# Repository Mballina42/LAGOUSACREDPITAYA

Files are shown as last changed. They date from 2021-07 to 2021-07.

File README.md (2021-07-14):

# HARDWARE PARA LAGO USAC CON RED PITAYA
Este proyecto recopila los avances realizados por [Escaramujo Project and LAGO Project matching hardware ](https://github.com/ECFM-USAC/EscaramujoLagoMatch), realizando cambios en el diseño de la PCB.

  

## Descripción
El diseño busca controlar el voltaje de alimentación para la placa de la base de un PMT Photonix, obteniendo la linea de alimentación principal de la Red Pitaya, a su vez enviar información de temperatura, presión barométrica y GPS. 

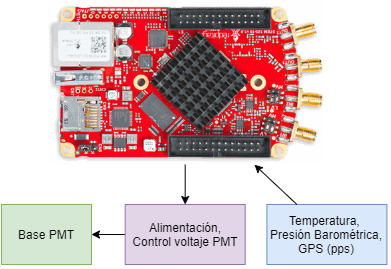
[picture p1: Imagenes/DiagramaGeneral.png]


Dado a que el tipo de voltaje necesitado por la base del PMT debe de ser lineal, la placa debe de proveer los siguientes voltajes:
* 5 VDC (MAX604)
* 3.3 VDC (MAX603)
* 12 VDC 
* 0 - 5 VDC variable
Esta placa se conecta a la base del PMT por medio de un conector RJ45.

Con base en el pinout de la Red Pitaya se utiliza los *pines IDE extension connector*

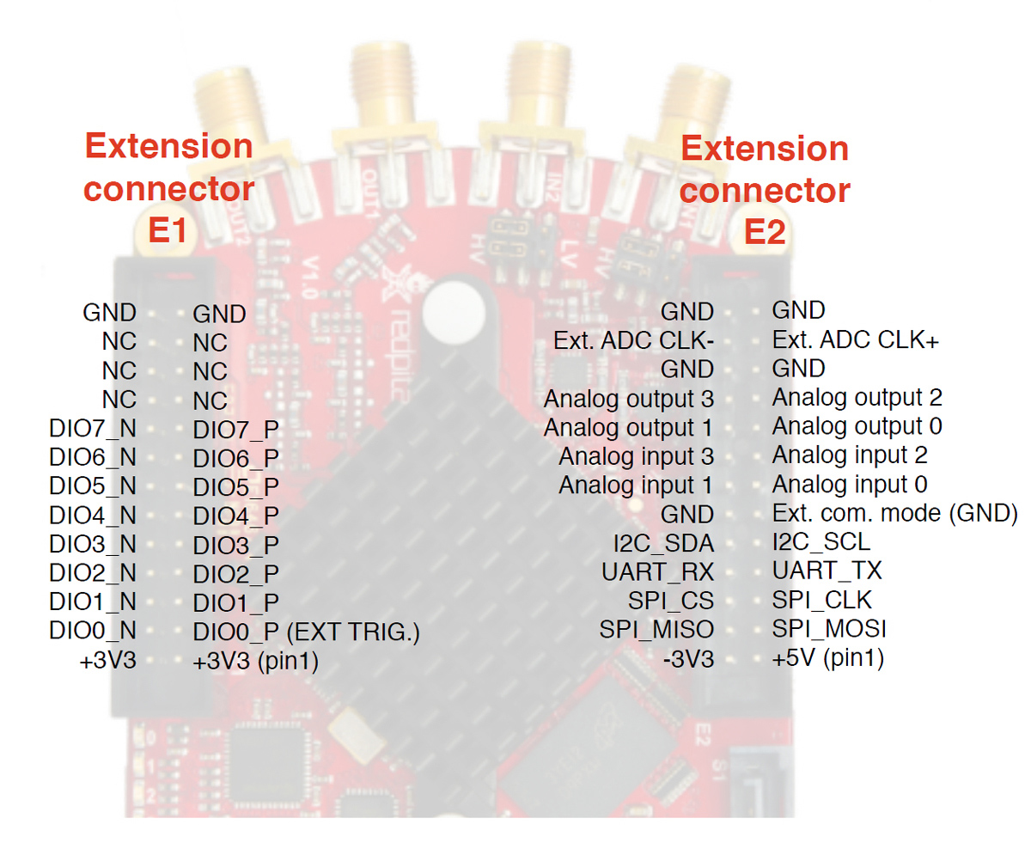
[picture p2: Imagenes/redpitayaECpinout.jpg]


La alimentación de la placa se obtiene del pin +5V.

Se utiliza el modulo BMP180 para la medición de presión barométrica y temperatura, conectado a la Red Pitaya por medio un conector RJ11 utilizando el protocolo de comunicación I2C, con los pines: I2C_SDA y I2C_SCL.

Se utiliza el modulo NEO-6M GPS, conectado por medio de HEADERS IDC y hacia la Red Pitaya por medio de UART_RX, UART_TX y DIO1_N.

Para el control del voltaje se utilizan los pines SPI_CS, SPI_CLK y SPI_MOSI.

[Este es el esquemático del proyecto en formato pdf](Imagenes/esquematico.pdf), también pueden consultarse los editables en la carpeta HARDWARE.

## Resultado final
El diseño del circuito y la PCB se realizaron en el software KiCad. Se muestra el modelo final de la PBC.

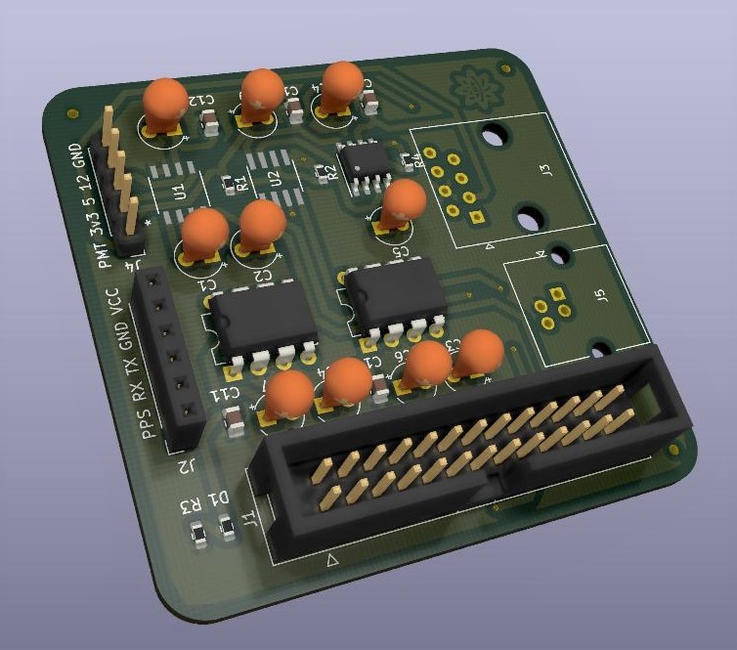
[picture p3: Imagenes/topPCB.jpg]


Dentro de la carpeta Gerber, se encuentra el gerber de cada parte del PCB y dentro de la carpeta CNC_code se encuentra el código para CNC elaborado en el software **FlatCAM**.

## License



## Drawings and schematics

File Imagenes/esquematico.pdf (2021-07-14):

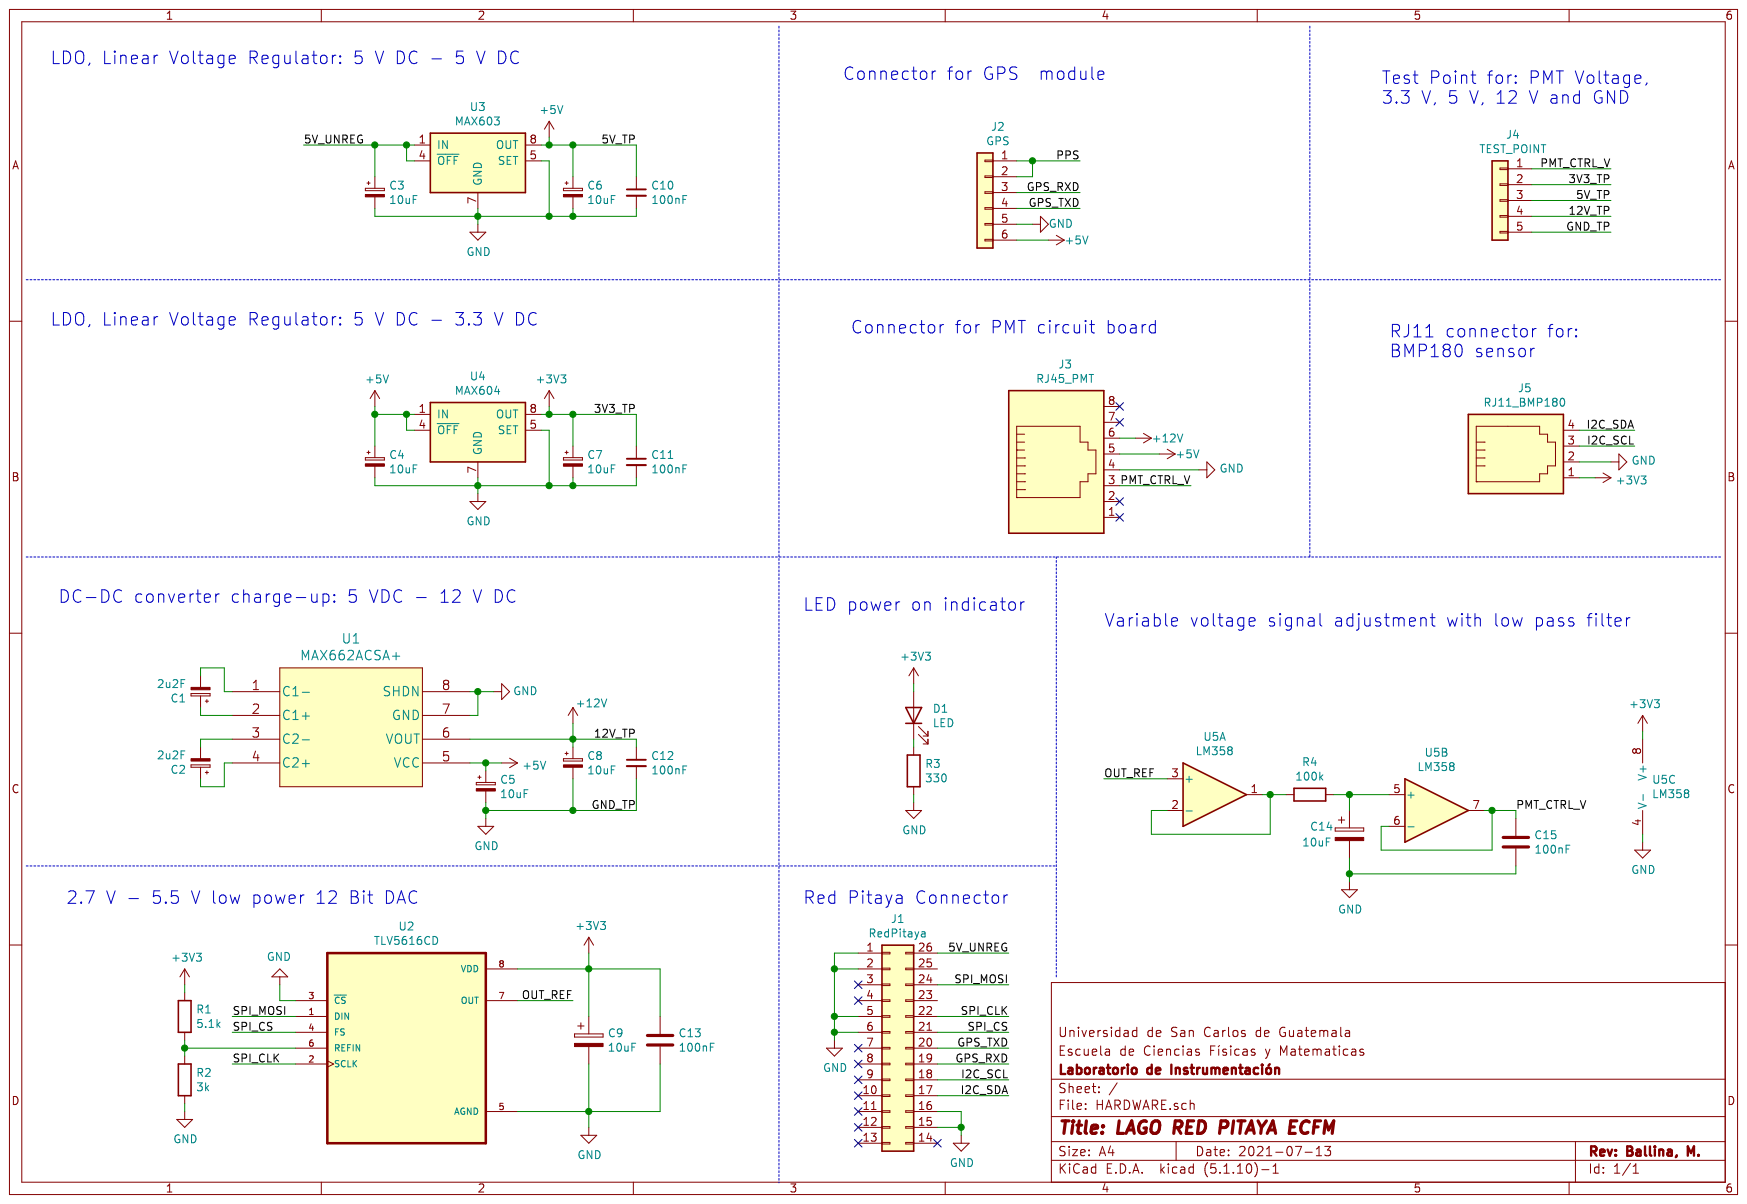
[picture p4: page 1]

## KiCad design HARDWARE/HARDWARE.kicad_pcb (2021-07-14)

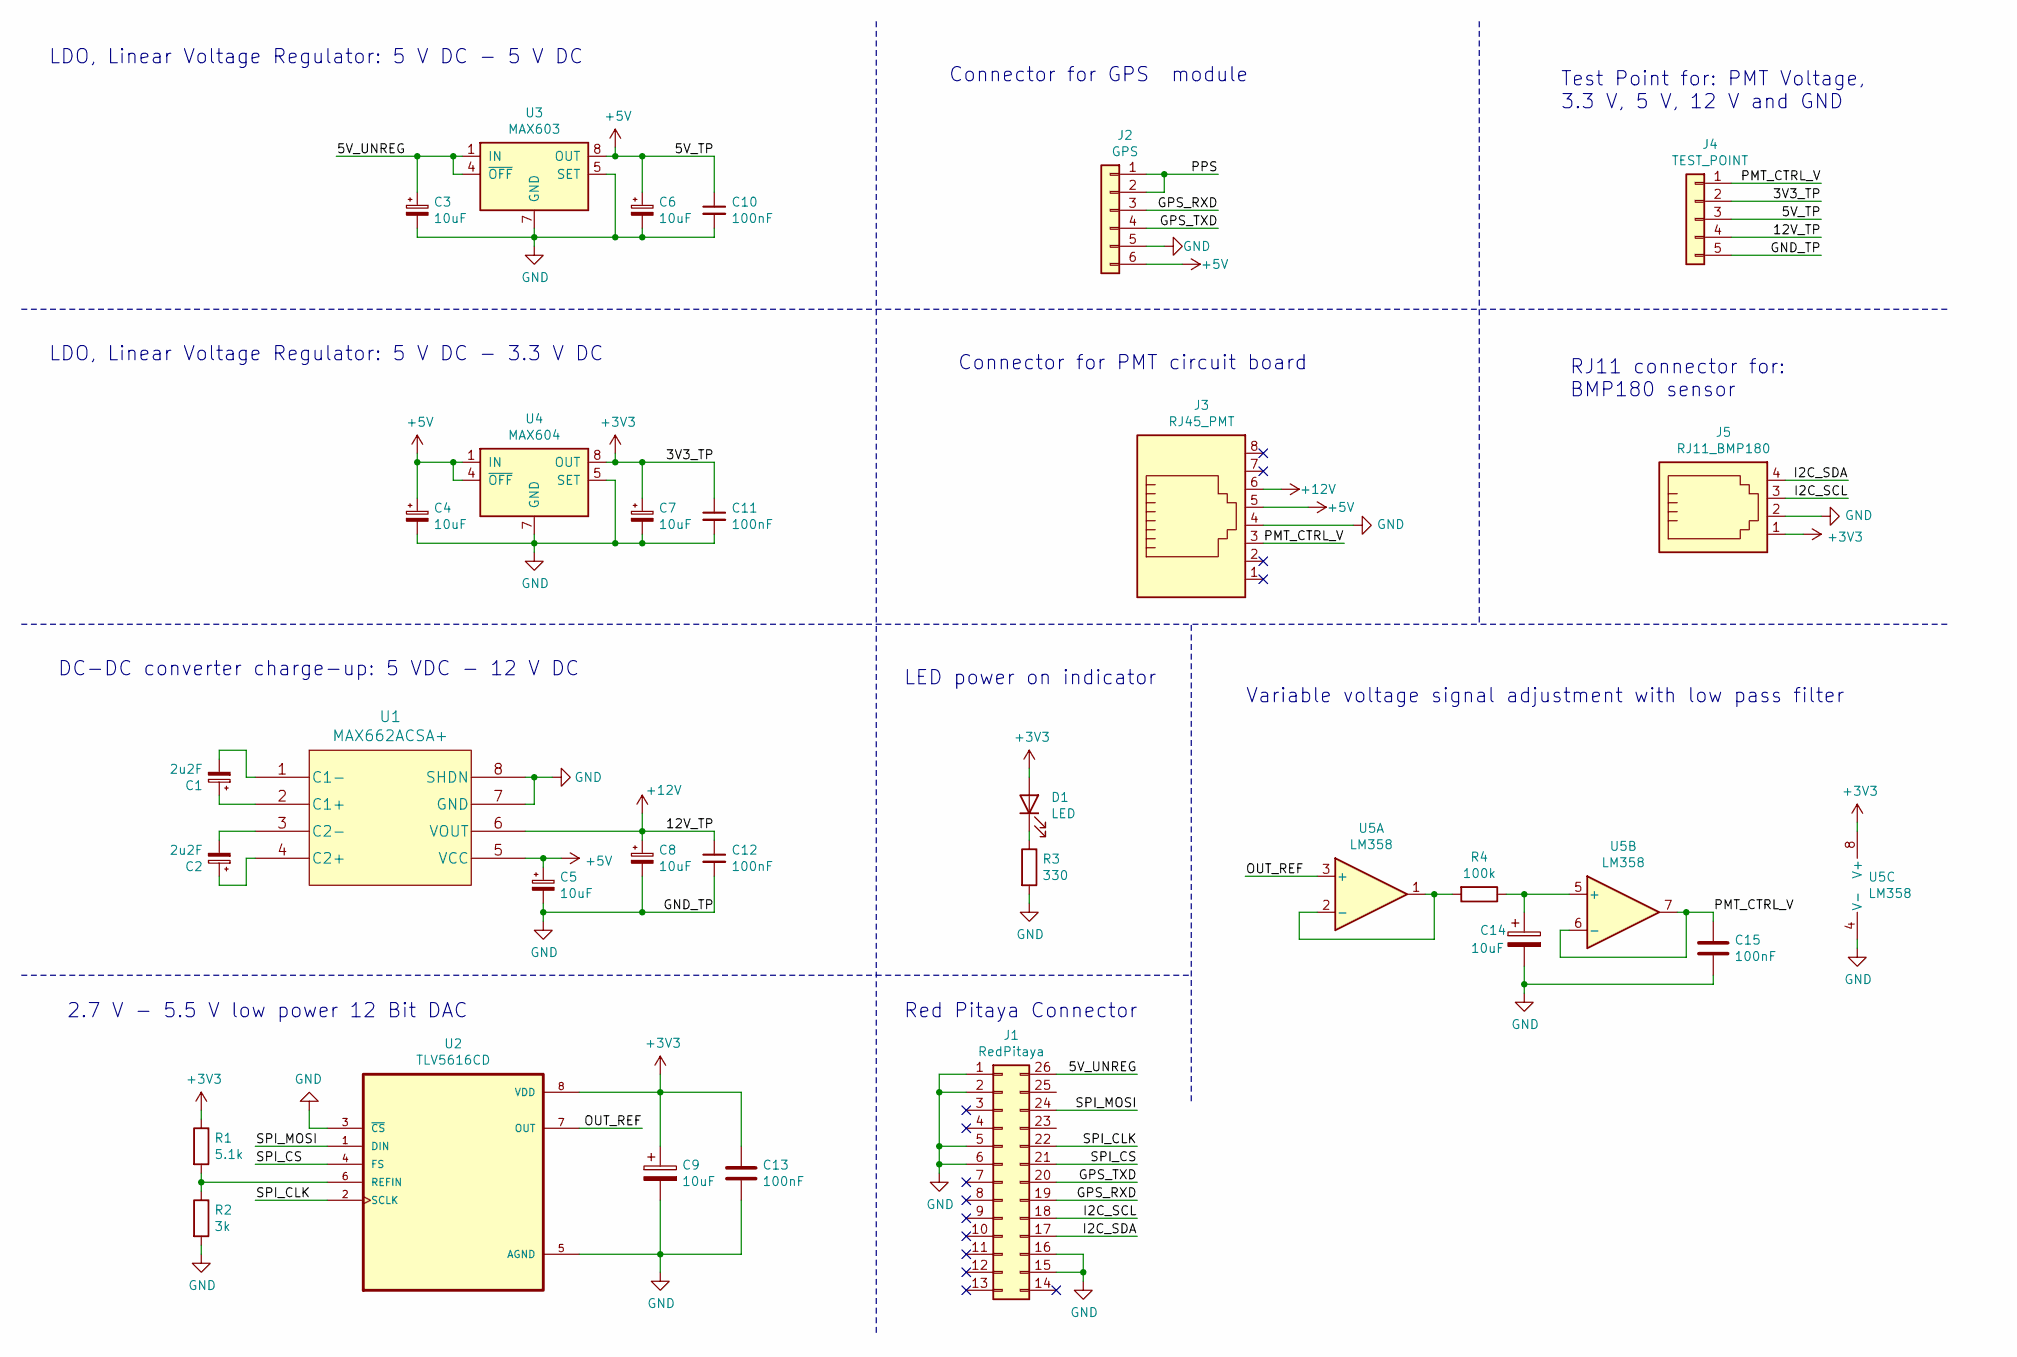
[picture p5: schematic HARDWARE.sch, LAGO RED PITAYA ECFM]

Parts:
C1, C2: 2u2F; CP_Radial_Tantal_D4.5mm_P2.50mm
C3, C4, C5, C6, C7, C8, C9, C14: 10uF; CP_Radial_Tantal_D4.5mm_P2.50mm
C10, C11, C12, C13, C15: 100nF; C_0805_2012Metric
D1: LED; R_0603_1608Metric
J1: RedPitaya; IDC-Header_2x13_P2.54mm_Vertical
J2: GPS; PinSocket_1x06_P2.54mm_Vertical
J3: RJ45_PMT; RJ45_Amphenol_54602-x08_Horizontal
J4: TEST_POINT; PinHeader_1x05_P2.54mm_Vertical
J5: RJ11_BMP180; RJ14_Connfly_DS1133-S4_Horizontal
R1: 5.1k; R_0603_1608Metric
R2: 3k; R_0603_1608Metric
R3: 330; R_0603_1608Metric
R4: 100k; R_0603_1608Metric
U1: MAX662ACSA+; MAX662ACSA&plus_
U2: TLV5616CD; SOIC127P599X175-8N
U3: MAX603; DIP-8_W7.62mm
U4: MAX604; DIP-8_W7.62mm
U5: LM358; SOIC-8_3.9x4.9mm_P1.27mm

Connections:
+3V3: C7.1, C9.1, C11.1, C13.1, D1.2 (A), J4.2, J5.1, R1.1, U2.8 (VDD), U4.8 (OUT), U5.8 (V+)
+5V: C4.1, C5.1, C6.1, C10.1, J2.6, J3.5, J4.3, U1.5 (VCC), U3.8 (OUT), U4.1 (IN), U4.4 (~OFF)
+12V: C8.1, C12.1, J3.6, J4.4, U1.6 (VOUT)
/5V_UNREG: C3.1, J1.26, U3.1 (IN), U3.4 (~OFF)
/GPS_RXD: J1.19, J2.3
/GPS_TXD: J1.20, J2.4
/I2C_SCL: J1.18, J5.3
/I2C_SDA: J1.17, J5.4
/OUT_REF: U2.7 (OUT), U5.3 (+)
/PMT_CTRL_V: C15.1, J3.3, J4.1, U5.6 (-), U5.7
/PPS: J2.1, J2.2
/SPI_CLK: J1.22, U2.2 (SCLK)
/SPI_CS: J1.21, U2.4 (FS)
/SPI_MOSI: J1.24, U2.1 (DIN)
GND: C3.2, C4.2, C5.2, C6.2, C7.2, C8.2, C9.2, C10.2, C11.2, C12.2, C13.2, C14.2, C15.2, J1.1, J1.2, J1.5, J1.6, J1.15, J1.16, J2.5, J3.4, J4.5, J5.2, R2.2, R3.2, U1.7 (GND), U1.8 (SHDN), U2.3 (~CS), U2.5 (AGND), U3.2 (GND), U3.3 (GND), U3.5 (SET), U3.6 (GND), U3.7 (GND), U4.2 (GND), U4.3 (GND), U4.5 (SET), U4.6 (GND), U4.7 (GND), U5.4 (V-)
unnamed: C1.1, U1.2 (C1+)
unnamed: C1.2, U1.1 (C1-)
unnamed: C2.1, U1.4 (C2+)
unnamed: C2.2, U1.3 (C2-)
unnamed: C14.1, R4.1, U5.5 (+)
unnamed: D1.1 (K), R3.1
unnamed: R1.2, R2.1, U2.6 (REFIN)
unnamed: R4.2, U5.1, U5.2 (-)

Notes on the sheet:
LDO, Linear Voltage Regulator: 5 V DC - 5 V DC
LDO, Linear Voltage Regulator: 5 V DC - 3.3 V DC
DC-DC converter charge-up: 5 VDC - 12 V DC
2.7 V - 5.5 V low power 12 Bit DAC
Connector for GPS module
Test Point for: PMT Voltage, 3.3 V, 5 V, 12 V and GND
Variable voltage signal adjustment with low pass filter
LED power on indicator
Red Pitaya Connector
Connector for PMT circuit board
RJ11 connector for: BMP180 sensor

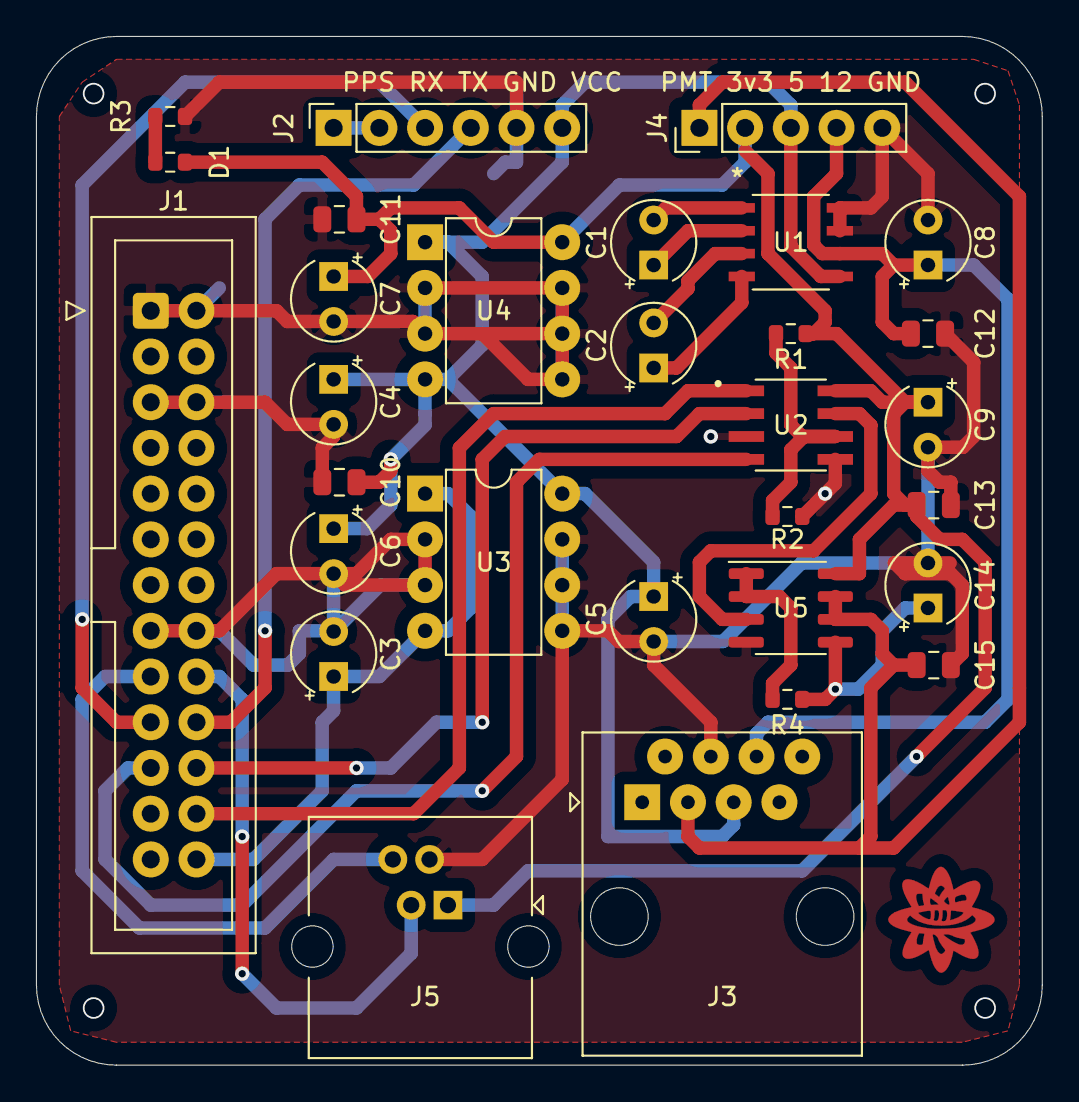
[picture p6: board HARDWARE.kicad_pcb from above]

Board: 2 copper layers, 55.9 x 57.1 mm, 30 parts (0 on the bottom side), 23 nets.

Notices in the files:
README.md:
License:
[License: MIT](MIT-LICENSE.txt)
